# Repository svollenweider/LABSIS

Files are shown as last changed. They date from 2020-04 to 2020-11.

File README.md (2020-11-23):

# LABSIS - WIP
Laboratory Monitoring System using an Arduino Nano 33 Iot. It records Temperature, Pressure, Humidity and Magnetic field. In addition it has connections to attach a 10kOhm thermistor, a flowmeter and a flood sensor as well as relays. 

# Arduino Library Prerequisites
- Adafruit BME280
- Adafruit MCP9808
- Dependencies of Adafruit BME280 and MCP9808
- Library for ALS31300.h (included)
- WiFiNINA
- RTCZero

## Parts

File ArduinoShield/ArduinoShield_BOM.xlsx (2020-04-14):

Item | Reference(s) | Qty | Manufacturer | MFG Part# | Description | Package | Type
1 | A1 | 2 | Samtec | SSW-115-01-T-S | CONN RCPT 15POS 0.1 TIN PCB | 15POS | THRU
2 | C1, C2, C3, C4, C5, C6 | 6 | MURATA | GRM033C80J104KE15D | CAP CER 0.1UF 10V X5R 0201 | 0201 | SMD
3 | D1 | 1 | Fairchild | MM3Z3V3B | DIODE ZENER 3.3V 200MW SOD323F | SOD-323F | SMD
4 | J1, J3 | 2 | Molex | 105313-1103 | Molex_Nano-Fit_105313-xx03_1x03_P2.50mm_Horizontal | 3POS | THRU
5 | J2, J4, J5 | 3 | Molex | 105313-1102 | Molex_Nano-Fit_105313-xx02_1x02_P2.50mm_Horizontal | 2POS | THRU
6 | J_3V3,JD1,J_GND1 | 3 | Any | Connector_PinHeader_2.54mm:PinHeader_1x04_P2.54mm_Vertical |  | 4POS | THRU
7 | J_A1 | 1 | Any | Connector_PinHeader_2.54mm:PinHeader_1x02_P2.54mm_Vertical |  | 2POS | THRU
8 | J_LED1, J_LED2 | 2 | Molex | 22232021 | K 254 Solid Header, Vertical, with Friction Lock | 2POS | THRU
9 | R1, R3, R5, R15, R16, R17 | 6 | Susumu | RR0306P-472-D | RES SMD 4.7K OHM 0.5% 1/20W 0201 | 0201 | SMD
10 | R2, R4, R6, R8, R10, R12, R13 | 7 | Susumu | RR0306P-103-D | RES SMD 10K OHM 0.5% 1/20W 0201 | 0201 | SMD
11 | R7 | 1 | Susumu | RR0306P-112-D | RES SMD 1.1K OHM 0.5% 1/20W 0201 | 0201 | SMD
12 | R9 | 1 | Susumu | RR0306P-471-D | RES SMD 470 OHM 0.5% 1/20W 0201 | 0201 | SMD
13 | R11, R14, R18, R19 | 4 | Susumu | RR0306P-561-D | RES SMD 560 OHM 0.5% 1/20W 0201 | 0201 | SMD
14 | U1 | 1 | Microchip | MCP9808T-E/MC | SENSOR DIGITAL -40C-125C 8DFN | DFN-8-1EP | SMD
15 | U2 | 1 | Allegro Microsystems | ALS31300EEJASR-2000 | SENSOR HALL EFFECT I2C | DFN-10-1EP | SMD
16 | U3 | 1 | Bosch | BME280 | SENSOR PRESSURE HUMIDITY TEMP | LGA-8 | SMD

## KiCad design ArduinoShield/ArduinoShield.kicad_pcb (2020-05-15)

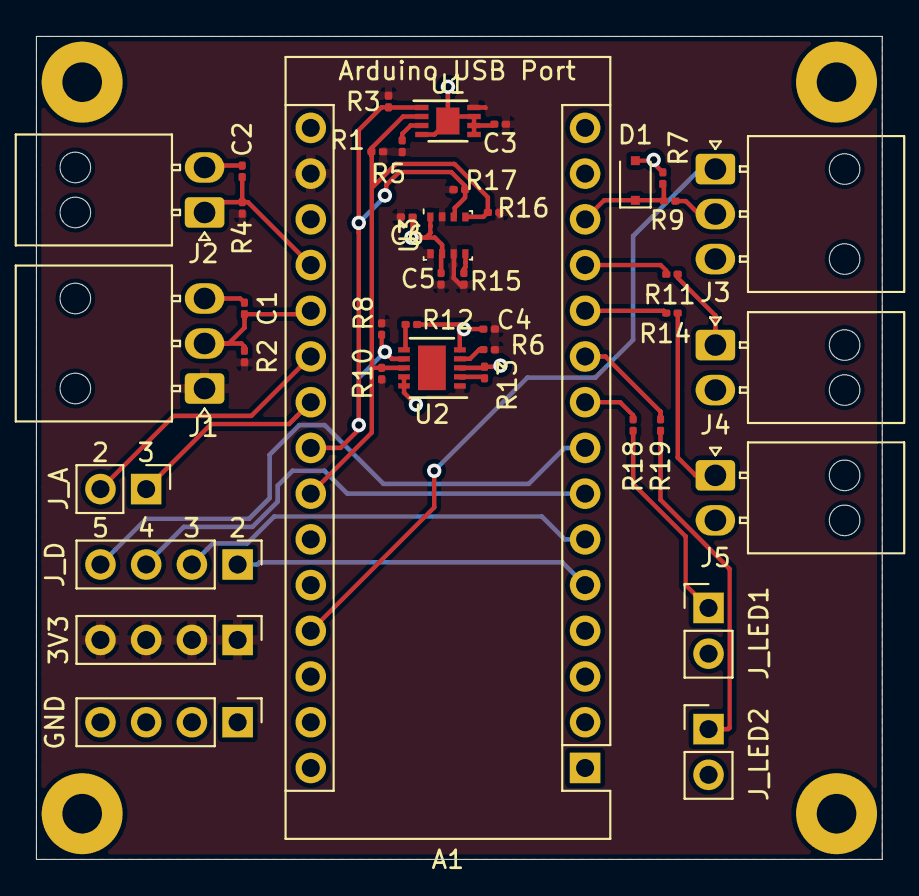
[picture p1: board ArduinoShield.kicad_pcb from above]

Board: 2 copper layers, 47.0 x 45.7 mm, 41 parts (0 on the bottom side), 28 nets.

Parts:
A1: Arduino_Nano_v3.x; Arduino_Nano
C1, C2, C3, C4, C5, C6: 100nF; C_0201_0603Metric
D1: MM3Z3V3B; D_SOD-323F
J1, J3: Molex 1053131103; Molex_Nano-Fit_105313-xx03_1x03_P2.50mm_Horizontal
J2, J4, J5: Molex 1053131102; Molex_Nano-Fit_105313-xx02_1x02_P2.50mm_Horizontal
J_3V3: 3V3; PinHeader_1x04_P2.54mm_Vertical
J_A1: J_A; PinHeader_1x02_P2.54mm_Vertical
J_D1: J_D; PinHeader_1x04_P2.54mm_Vertical
J_GND1: GND; PinHeader_1x04_P2.54mm_Vertical
J_LED1, J_LED2: PinHeader1x02; PinHeader_1x02_P2.54mm_Vertical
R1, R3, R5, R15, R16, R17: 4.7k; R_0201_0603Metric
R2, R4, R6, R8, R10, R12, R13: 10k; R_0201_0603Metric
R7: 1.1k; R_0201_0603Metric
R9: 470R; R_0201_0603Metric
R11, R14, R18, R19: 562R; R_0201_0603Metric
U1: MCP9808_DFN; DFN-8-1EP_3x2mm_P0.5mm_EP1.3x1.5mm
U2: ALS31300; DFN-10-1EP_3x3mm_P0.5mm_EP1.55x2.48mm
U3: BME280; Bosch_LGA-8_2.5x2.5mm_P0.65mm_ClockwisePinNumbering

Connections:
+3V3: A1.17, C3.1, C4.2, C5.1, C6.1, J1.1, J_3V3.1, J_3V3.2, J_3V3.3, J_3V3.4, R1.1, R2.1, R3.1, R4.1, R5.1, R6.1, R8.1, R10.1, R15.1, R16.1, R17.1, U1.8, U2.1, U3.2, U3.6, U3.8
+5V: A1.27, J3.1
A2: A1.21, J_A1.2
A3: A1.22, J_A1.1
AFloodMeas: A1.20, C1.1, J1.2, R2.2
ATempMeas: A1.19, C2.1, J2.1, R4.2
D2: A1.5, J_D1.1
D3: A1.6, J_D1.2
D4: A1.7, J_D1.3
D5: A1.8, J_D1.4
DFlow: A1.13, D1.1, R7.1, R9.1
GND: A1.4, A1.29, C1.2, C2.2, C3.2, C4.1, C5.2, C6.2, D1.2, J1.3, J2.2, J3.3, J4.2, J5.2, J_GND1.1, J_GND1.2, J_GND1.3, J_GND1.4, J_LED1.2, J_LED2.2, R7.2, R12.2, R13.2, U1.4, U1.5, U1.6, U1.7, U1.9, U2.3, U2.5, U2.9, U2.10, U3.1, U3.7
LED1: A1.9, R18.1
LED2: A1.10, R19.1
unnamed: J3.2, R9.2
unnamed: J4.1, R11.2
unnamed: J5.1, R14.2
unnamed: J_LED1.1, R18.2
unnamed: J_LED2.1, R19.2
unnamed: R5.2, U1.3
unnamed: R6.2, U2.4
unnamed: R12.1, U2.6
unnamed: R13.1, U2.2
unnamed: R15.2, U3.5
Relay1: A1.11, R14.1
Relay2: A1.12, R11.1
SCL: A1.24, R1.2, R10.2, R16.2, U1.2, U2.8, U3.4
SDA: A1.23, R3.2, R8.2, R17.2, U1.1, U2.7, U3.3

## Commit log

2020-03-23 Added Schematics and PCB
    [ArduinoShield.kicad_pcb, ArduinoShield.sch]
2020-03-30 Small changes to design, added BOM
    [ArduinoShield.kicad_pcb, ArduinoShield.sch, ArduinoShield_BOM.xlsx]
2020-04-08 Completed BOM
    [ArduinoShield_BOM.xlsx]
2020-04-08 Fixed BOM, added Gerber File export
    [ArduinoShield.kicad_pcb, ArduinoShield_BOM.xlsx]
2020-04-14 Updated Hole size for Arduino, Created Footprint for bigger hole sizes
    [ArduinoShield.kicad_pcb, ArduinoShield.sch, ArduinoShield_BOM.xlsx]
2020-05-15 Modified part that was wrong in KiCad Library (MCP9808)
    [ArduinoShield.kicad_pcb, ArduinoShield.sch]
2020-05-15 Fixed merging issues
    [ArduinoShield.kicad_pcb, ArduinoShield.sch]
2020-05-15 Final Fix for pcb
    [ArduinoShield.sch]
